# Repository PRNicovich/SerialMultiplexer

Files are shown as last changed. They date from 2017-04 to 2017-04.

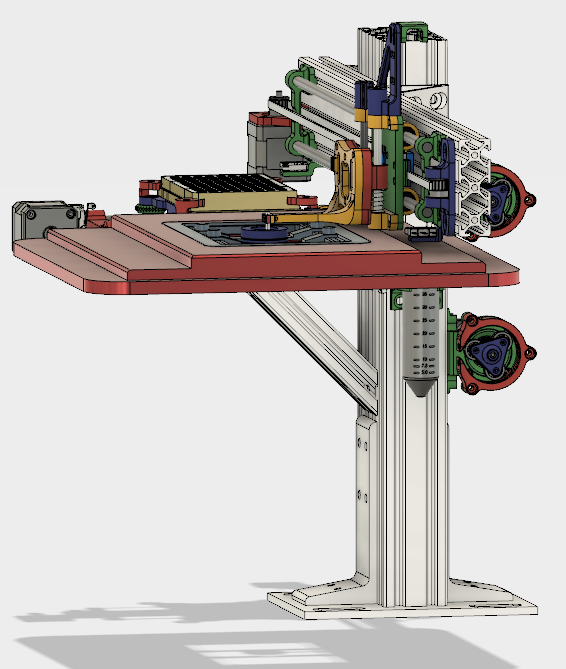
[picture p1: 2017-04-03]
Pics/Renderings/Full assembly right front.png

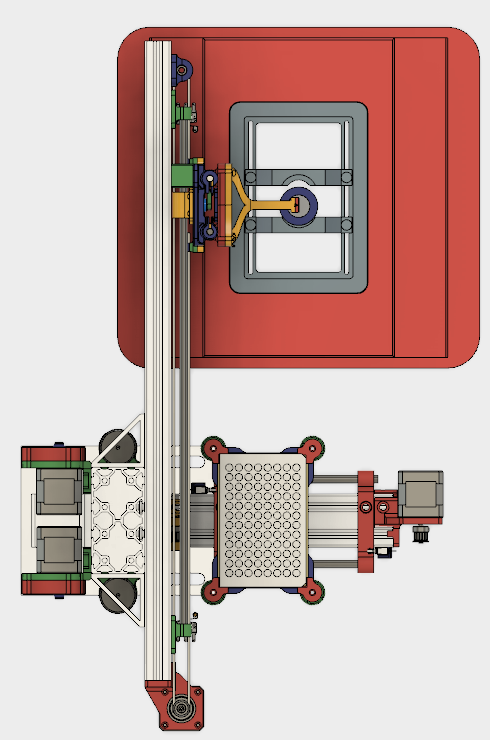
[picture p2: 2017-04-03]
Pics/Renderings/Full assembly top.png

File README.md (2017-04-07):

# Open source robot for liquid handing and serial multiplexing fluorescence microscopy

### Motivation

For fluorescence microscopy, a large limitation on the amount of data that can be extracted from a single sample is the number of targets that can be labeled within a sample.  Fluorophore spectral overlap limits this to around four targets in a typical setup, possibly up to ten if careful spectral demixing is done. In contrast, a single signalling pathway may contain a few hundred components.  Quantifying all of these components in a single sample would require an approach that increases the number of targets by an order of magnitude or more.  

One solution is to label targets in a sequential manner with probe signal nullification steps in between.  Target probes are introduced in sequential rounds, if possible without moving the sample off of the microscope.  After imaging, the probe signal can be removed either by stripping the probes, washing out the probe solution, or chemically or photo-bleaching the label fluorophore.  With this procedure the number of targets that can be probed is expanded with the number of rounds.  With a 4 color set-up and 10 rounds, for example, there are up to 40 target channels that can be captured in such an experiment.  With clever 'barcoding' schemes, this can even scale exponentially, rather than linearly, with the number of rounds.  

To accomplish this feat, a single sample must be processed through the labelling and stripping steps repeatedly. Doing so automatically avoids many hours of exceptionally tedious work and ultimately a more precise product.  For this a form of multi-channel liquid handling is required.  To further avoid spending tens of thousands of dollars on a project that was initially unsanctioned and unfunded, a low-cost solution is certainly a benefit.

## Approach 

The *in situ* automated liquid handing needs to be able to move a selected aliquot of solution from one place off of the microscope into the sample holder.  Then this aliquot needs to be removed, the sample washed with buffer, possibly multiple times, while removing the waste solution.  Then the cycle needs to repeat.  Were this done manually, solutions would be pre-mixed in microcentrifuge tubes or a well plate.  An operator would then remove solution from each well in turn and adding to the sample holder, interspersing washing and waste removal steps.  This would likely be done with a micropippetor and disposable tips.  

Recapitulating this closely with a robotics platform is certainly a straightforward approach.  The micropippetor could even be mounted on a gantry arm and moved between the reagent and sample locations.  Such an action is the basis of many pipetting robots.  However, the volume setting and tip ejection are motions adding extra complexity that may not be required.  If instead liquid was dosed out of a programmable pump through a reusable tip, the setting and ejection steps would be unnecessary.  The remaining motions are then to position this tip into the reagent well and then into the sample chamber with dosing via the pumps.  This forms the basis of the design here.

The liquid-handling head (actually made of 3 separate tips, detailed below) is on a carrier head.  This head has a servo motor for raising and lowering, essentially toggling between two positions.  The carrier is on a long axis that moves it from the reagent well plate location to the sample on the microscope, some distance (~450 mm) away.  The well plate is on a holder that places the base of this plate and the bottom of the sample holder in the same plane.  The well plate holder is on its own carrier on a shorter axis that allows a given row of the well plate to be selected (the first axis selects the column).  An aliquot is drawn into the liquid handling head by a pump, which then pushes to dispense this liquid at the sample.  A second tip in this head can dispense buffer from a reservoir, and a third withdraws waste.  The first pump operates in a toggle-like mode, with the second and third in a unidirectional motion only.  The grand total is then a servo, three "positioning" motors, and two "dispensing" motors. 

Turns out this list also makes a 3D printer.  The carrier axes correspond to XY, the reagent toggle pump the Z axis, and the buffer and waste pumps taking the role of a dual extruder.  The positioning precision of a hobby-level 3D printer is plenty for this application.  An open-source RAMPS controller built upon an Arduino Mega supports these 5 stepper motors, the servo, plus a bit of additional functionality, with communication over a USB serial with G code commands.  The design can capitalize on the 3D printer hobbyst community and the cheap components available for those projects.  These include the controller, motors, bearings, guide rods, and timing belts.  A bit of extruded T slot aluminum makes up the bulk of the skeleton, with the remaining parts being 3D printed on a desktop machine.

The bulk of the complex parts can be printed on a standard filament 3D printer.  This borrows quite bit again from the hobbyst 3D printer community, specifically the Reprap and Prusa projects.  Many of the components were highly inspired by analogous components in these projects.  

Controller code is based on Marlin (with configurating settings to work with this build) just as many Reprap printers.  The PC communicates with the controller through G code commands in this software.  A MATLAB class and demo scripts simplifying these operations will be included though one could imagine a custom fork of something like Repetier to drive the instrument.  From our perspective mounting the device within MicroManager or similar instrument-driving software is the eventual goal for integration into a microscope platform. 

To complete the liquid handling side of the machine, 3D printable peristaltic pumps were designed.  The use of the same stepper motors make these easy to control.  The controller is already set up to treat these as either the Z printer axis or a dual-head extruder.  The design uses skate bearings against flexible tubing to push along fluid.  These have no issue moving an appropriate amount of fluid in a reasonable time under PC control. There is a decent amount of pulsing but it is sufficient for moving fluid from one place to another. One could substitute these for syringe pumps or another, more precise, fluid-moving system if desired.  The Arduino has multiple serial ports exposed that could be addressed (or this could be handled on the PC side) to send commands to such pumps if not driving the motor directly. 

## Design considerations

The use of 3D printed parts and components is not the most precise way to do things.  The combination of rough parts and slop in cheap bearings is plenty to have extra motion above the theoretical resolution.  To address this, one must focus first on what precision is actually needed.  Here the XY positioning needs to be good enough to not hit the wall of the plate well.  The chosen steppers, drivers, and belt can theoretically hit 180 micrometer positioning.  Our tests show repeatability within 2-3x this, though periodic axis re-zeroing is a good idea to avoid missing step errors.  Still that is certainly precise enough to hit the middle of a well that's approximately 5 mm in diameter.

More precision is needed for the up-down motion of the needle carrier head.  Or, more correctly, the lower limit of this travel must be precise and repeatable to reach as close of the bottom of the well as possible to avoid wasting liquid (at the other end, as long as the needle is high enough up it doesn't matter where it is past that).  The same criterium means that solution removal and washes at the sample chamber can be more efficient.  There is an additional wrinkle in that the bottom of the sample chamber is a very thin, fragile glass coverslip.  Slamming into that repeatedly will lead to a crack and ruined experiment.  So we need a way to repeatably hit the same position without overshooting at the end of the downstroke for the bottom of the well and the bottom of the sample chamber. 

The second consideration for a "sloppy" system can be applied to simplify this issue, namely to leave enough adjustment to fine-tune or calibrate any residual imprecision out of the system.  The design is intended to hold the bottom of the well plate in the same plane as the bottom of the sample chamber.  This removes the need for separate positioning for the two locations, meaning there is only one bottom position for the needle carrier to hit.  The transverse X axis can be moved up and down on the vertical support member to roughly position the needle carrier in the proper vertical position for the associated microscope stage.  The well plate axis can slide along the same vertical member to bring the well plate in the same plane as the sample.  Finally there is a finer adjustment in the carrier head, where the linkage between the servo linkage arm can vertically translate in the needle carrier to bring the stop position in the proper alignment. 

Initially the linkage between the servo motor and the needle axis was a cam-follower mechanism.  The servo would rotate and push against a pair of springs around the bearing rods to lower the needle carrier.  This has the distinct advantage in that an imprecise rotator (a cheap servo) can lower to the same position very repeatedly.  If the cam is a constant diameter through a range at the end of the travel, as long as the rotation is somewhere in that range then the translation imprecision is removed.  Unfortunately finding appropriate springs of the proper diameter and length and compression force is difficult and time-consuming, so this approach was abandoned. 

The alternate approach was a more traditional linkage between the servo and needle carrier.  Now the servo rotational position is directly tied to the translation position.  The error in this rotatation is also directly linked.  In practice the cheap servo used does work within the repeatedly required. When moving long distances there is a considerable amount of rotational overshoot, however, which seems to be proportional to the distance traveled.  This may be minimized with a higher-quality motor or proper servo controller, but one work-around is to move in steps. The bulk of the motion can be done in a first step, but stopping early so that overrotation of the servo does not result in overshooting the final target.  A second smaller step brings the needle carrier to the final position with much lower overshoot.  This effect is visible in the included video of the instrument in action where the vertical motion of the needle carrier is clearly done in two motions.

Motor positions and travel speeds can be set in software.  These need to be calibrated for the given build.  For travel of the axes this is straighforward and in millimeters.  Rotational position of the servo and translation of dispensor distance to volume units will need to be done empirically, but this is relatively straightforward to establish. 

## Repo contents

.\STEP Files\ - STEP files of full assembly and of the custom base plate to mount to a metric optical table.  

.\STL Files\ - All files for 3D printing.  These are ready to go into your favorite slicer software to generate 3D printer machine code.

.\Pics\ - Photos and renderings of the completed assembly.  A video of the robot motion testing in action is included. 

.\Hardware\ - Bill of Materials for all items to be purchased for this build.  This includes all fasteners and other hardware omitted in the STEP files.  A measured drawing for the base plate is included, ready to be sent to your local machine shop (or give making it yourself a shot). 

.\Code\ - Configuration files for Marlin driver for Arduino and MATLAB PC-side MATLAB code included.  The PC does a small amount of processing and primarily relays Gcode over a serial connection to the Arduino.  Should be straightforward to port to Python, Micromanager Beanshell Java, or whatever other language you may prefer.

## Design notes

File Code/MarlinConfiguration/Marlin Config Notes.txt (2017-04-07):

Download latest stable release of Marlin from associated Github repo:

https://github.com/MarlinFirmware/Marlin/releases

Configuration guide can be found here:

https://github.com/MarlinFirmware/Marlin/wiki/Marlin-Configuration

The two files in this folder, Configuration.h and Configuration_adv.h, are those from the original implementation of this build.  You can replace the default Marlin config files with these as a good starting point.  These include important details about temperature sensors (or the lack thereof) and end stops. Further tweaks can be made if desired to tune specifically for your project.

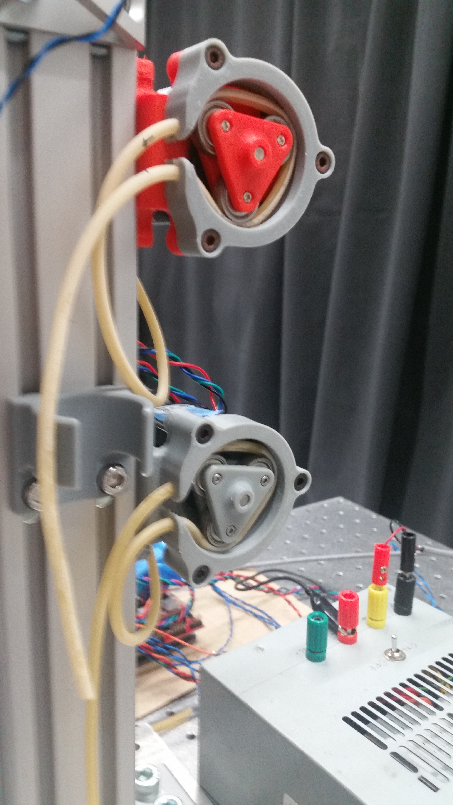
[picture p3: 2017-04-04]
Pics/Photos/PumpHeads.jpg

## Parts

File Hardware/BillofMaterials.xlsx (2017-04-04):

Category | Description | Supplier | Supplier part no | Qty | Price per | Total cost | Notes
T slot profiles | 25 mm x 75 mm T slot | 80/20 | 25-2576 | 1 | $19.98 | $19.98 | 600 mm; tap all holes on ONE end
 | 50 mm x 100 mm T slot | 80/20 | 25-5010 | 1 | $19.50 | $19.50 | 435 mm
 | Angle anchor bracket | 80/20 | 25-2416 | 2 | $11.05 | $22.10
 | 4 bolt angle support | 80/20 | 25-4138 | 2 | $7.45 | $14.90
 | 45 degree angle profile | 80/20 | 25-2566 | 1 | $14.95 | $14.95
 | 25 mm x 50 mm T slot | 80/20 | 25-2550 | 1 | $12.91 | $12.91 | 233 mm; tap holes on one end; contersink 2 holes on wide face other end
 | Cam connectors | 80/20 | 25-3363 | 2 | $4.00 | $8.00
 | T slot nuts | 80/20 | 25-1962 | 30 | $0.23 | $6.90
 | T slot nuts, double | 80/20 | 25-1941 | 12 | $0.53 | $6.36
Motion surfaces | LM8UU bearings | CNC Superstore | LM8UU | 4 | $1.49 | $5.96
 | LM6UU bearings | CNC Superstore | LM6UU | 2 | $1.49 | $2.98
 | SKF 625 bearings | VXB | 625-Z | 13 | $1.49 | $19.37 | Open or sealed OK
 | 682 bearings | VXB | KIT7420 | 2 | $6.49 | $12.98 | Open > sealed
 | GT2 pulleys | MakerTechStore | n/a | 4 | $3.00 | $12.00 | 16 teeth; 5 mm bore
 | GT2 belt | MakerTechStore | n/a | 7 | $2.50 | $17.50 | 7 ft, 2 m; 2 mm pitch
 | Bearing rods; 6 mm x 100 mm | VXB | SNS6X100MM-NB | 2 | $19.95 | $39.90 | 100-150 mm
 | Bearing rods; 8 mm x 500 mm | VXB | KIT11866 | 2 | $19.95 | $39.90 | 480-550 mm (product is 495 mm)
 | Bearing rods; 8 mm x 150 mm | eBay | various | 2 | $5.00 | $10.00 | 150-170 mm
 | Well axis clamp springs | McMaster-Carr | 9657K81 | 4 | $5.43 | $21.72 | 3.5-4.5 mm dia; 3-6 mm compressed length
Motors | NEMA 17 steppers | Various | Various | 5 | $20.00 | $100.00 | 1.8 deg step (200/rev); 45 N-cm (64 oz-in)
 | Micro servo | Various | Various | 1 | $6.00 | $6.00 | 5V; 9g; Tower Pro SG92R or similar
Fasteners | M10 SHCS | McMaster-Carr | 91290A127 | 4 | $7.29 | $7.29 | 14 mm, pk of 25
 | M6 SHCS | McMaster-Carr | 91290A330 | 8 | $7.28 | $7.28 | 25 mm, pk of 50
 | M6 BHCS | McMaster-Carr | 91239A316 | 60 | $10.14 | $10.14 | 10 mm, pk of 100
 | M5 SHCS | McMaster-Carr | 91292A193 | 2 | $5.37 | $5.37 | 35 mm, pk of 25
 | M4 SHCS | McMaster-Carr | 91292A118 | 10 | $7.20 | $7.20 | 16 mm, pk of 100
 | M3 SHCS | McMaster-Carr | 91292A113 | 50 | $4.40 | $4.40 | 10 mm, pk of 100
 | M3 SHCS | McMaster-Carr | 91292A020 | 12 | $6.40 | $6.40 | 25 mm, pk of 100
 | M2 SHCS | McMaster-Carr | 91292A834 | 8 | $3.64 | $3.64 | 12 mm, pk of 100
 | M2 SHCS | McMaster-Carr | 91292A832 | 18 | $6.00 | $6.00 | 8 mm, pk of 100
 | M2 SHCS | McMaster-Carr | 92290A012 | 2 | $6.72 | $6.72 | 5 mm, pk of 100
 | M2 washers | McMaster-Carr | 93475A195 | 2 | $1.06 | $1.06 | pk of 100
 | M2 nuts | McMaster-Carr | 90592A004 | 21 | $1.04 | $1.04 | pk of 100
 | M3 washers | McMaster-Carr | 93475A210 | 4 | $1.62 | $1.62 | pk of 100
 | M3 nuts | McMaster-Carr | 90591A250 | 50 | $2.06 | $2.06 | pk of 100
 | M4 nuts | McMaster-Carr | 90591A255 | 10 | $2.28 | $2.28 | pk of 100
 | M5 nuts | McMaster-Carr | 90591A260 | 2 | $2.61 | $2.61 | pk of 100
Cable carrier | 10 x 15 mm segmented carrier | Sparkfun | 13207 | 1 | $10.95 | $10.95
Tubing | 2 mm x 4 mm tubing | McMaster-Carr | 5186T11 | 20 | $0.65 | $13.00 | 3 m (20 ft); 2 mm ID, 4 mm OD
 | 1.0 mm x 2 mm tubing | McMaster-Carr | 51825K41 | 25 | $0.21 | $5.25 | 25 ft; 1 mm ID, 2 mm OD
 | 18ga stainless tubing | McMaster-Carr | 50415K38 | 1 | $8.80 |  | 0.5 m; 18 gauge blunt needles w/ flange cut work well!
Controller | RAMPS 1.4 board | Various | -- | 1 | $10.00 | $10.00
 | Arduino Mega | Various | ATmega2560 R3 board | 1 | $9.00 | $9.00
 | Stepper controller | Various | A4988 module | 5 | $1.50 | $7.50
 | 5v/12v power supply | Various | -- | 1 | -- | -- | home-built from PC PSU
 | Connection wires | Various | -- | varies | $10.00 | $10.00 | est
 | Spade connector (F) | Mouser | 534-1252 | 8 | $0.15 | $1.20 | Many similar connectors
Limit switches | Omron D2SW‑P2L2T | Mouser | 653-D2SW-P2L2T | 4 | $3.04 | $12.16
Mounting plate | Machined mounting plate | ProtoLabs | -- | 1 | $251.39 | $251.39 | See ..\STEP Files\ModifiedBase.stp, .\OpticalTableTslotMountingPlate_Sheet1.pdf
 |  |  |  |  | Total | $819.47 | ← Surely an over-estimate, as: - the mounting plate can be made to MUCH larger tolerance than quoted - steppers cheaper if bought in a larger group - likely can find cheaper source for bearing shafts - most screws ordered in excessively large packs

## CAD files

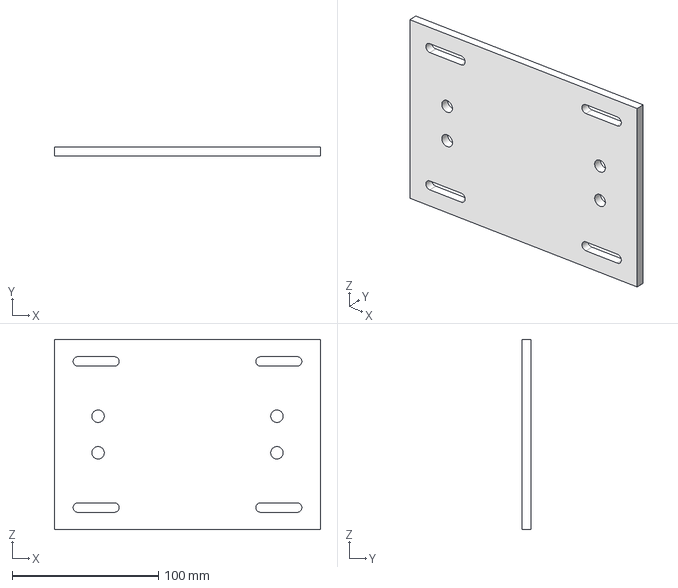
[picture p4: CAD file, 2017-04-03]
STEP Files/ModifiedBase.stp
182.0 x 6.00 x 130.0 mm

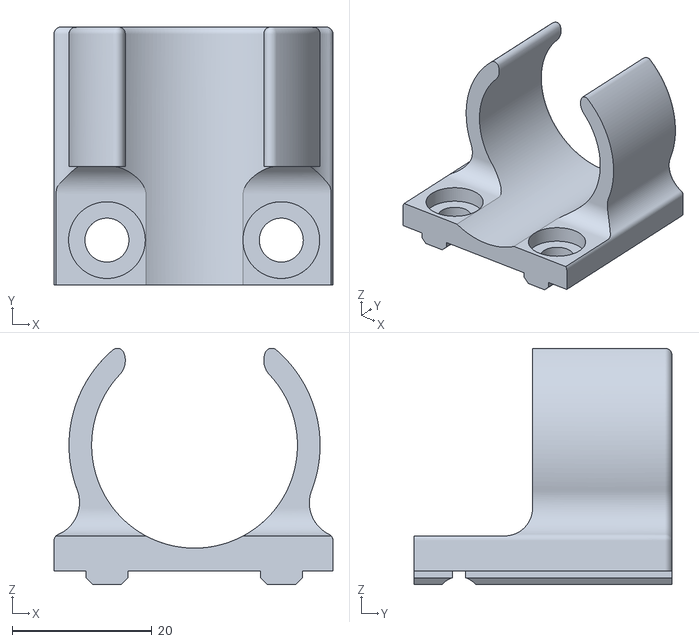
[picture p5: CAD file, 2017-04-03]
STL Files/Attachments/50mLTubeHolder.stl
40.0 x 37.0 x 33.9

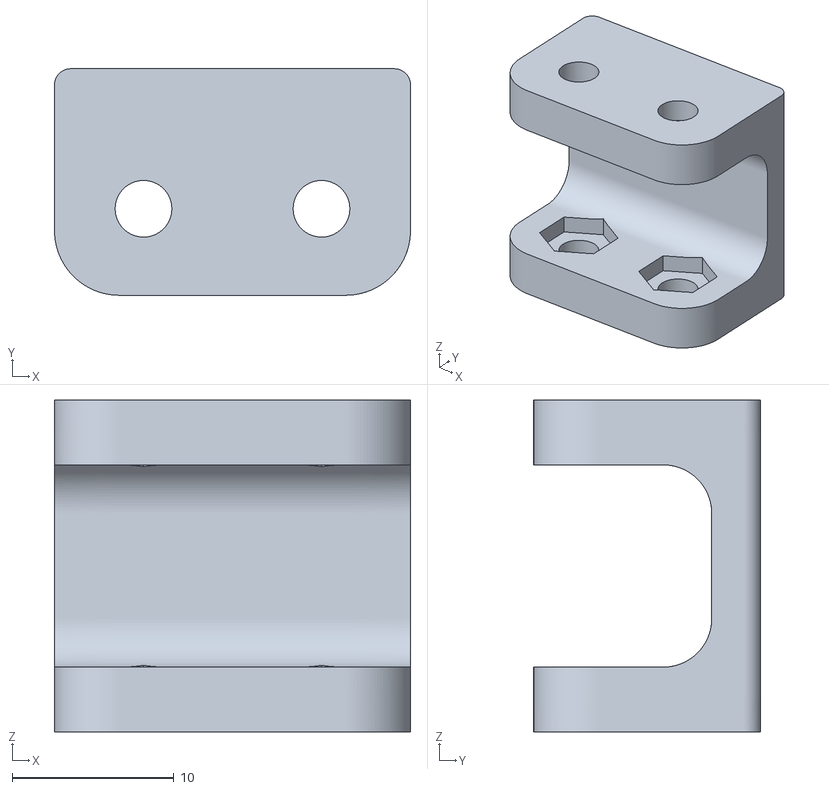
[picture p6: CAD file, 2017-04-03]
STL Files/CarrierAxis/Cable carrier to cable snake.stl
22.0 x 14.0 x 20.5

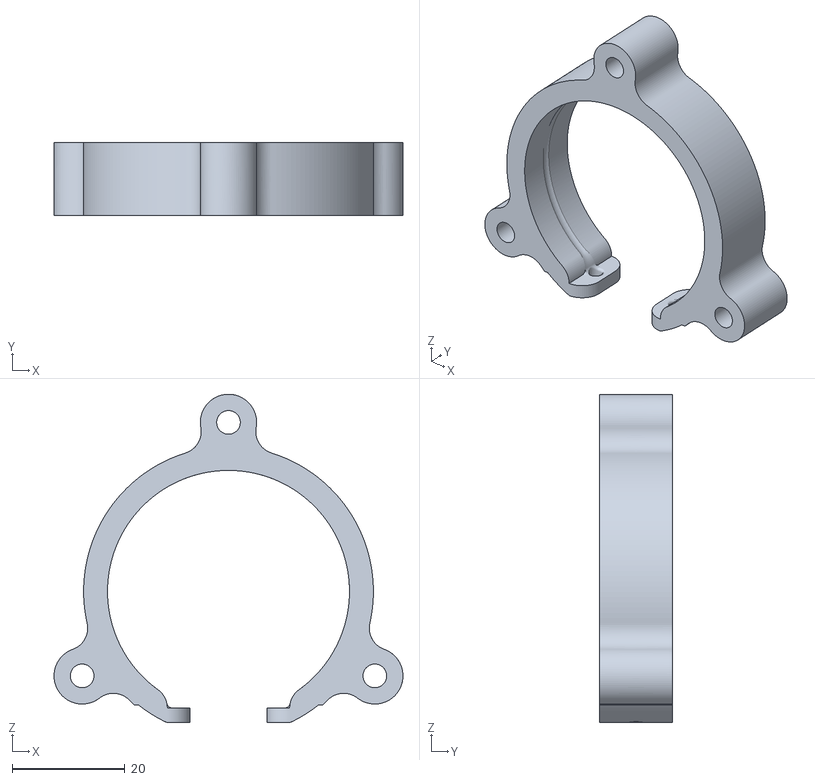
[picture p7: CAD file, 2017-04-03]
STL Files/PerfusionPump/PumpChassis.stl
62.0 x 13.0 x 58.3

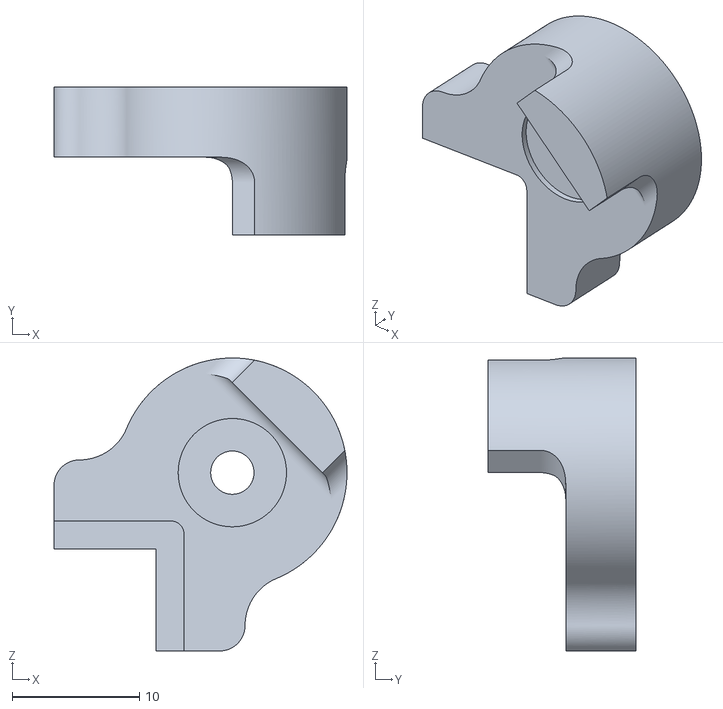
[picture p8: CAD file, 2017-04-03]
STL Files/WellPlateAxis/WellPlateClampRetry.stl
23.0 x 11.6 x 23.0

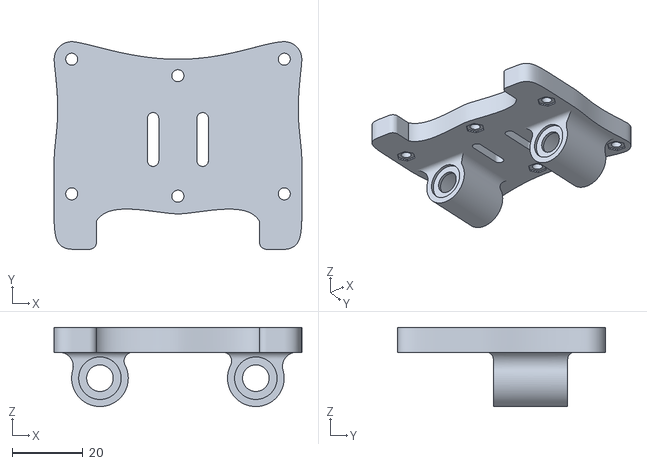
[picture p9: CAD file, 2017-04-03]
STL Files/CarrierAxis/NeedleCarrier.stl
70.0 x 58.6 x 22.3

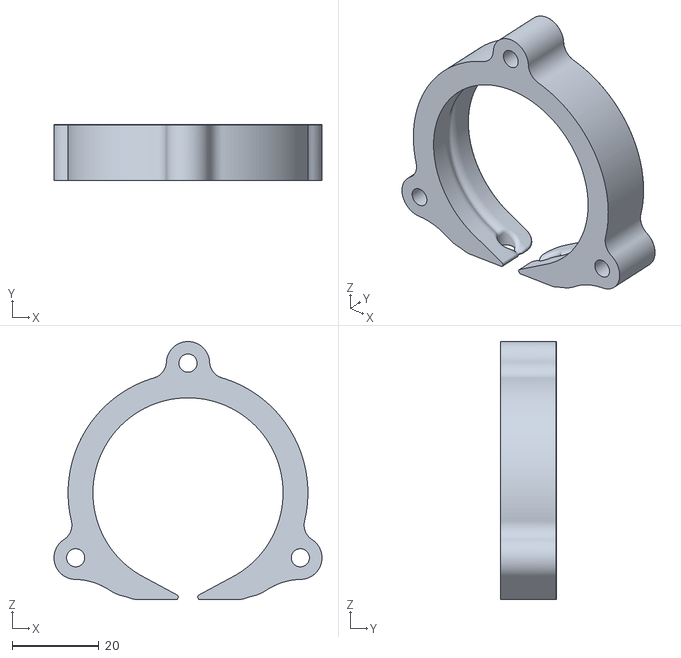
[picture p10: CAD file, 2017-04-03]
STL Files/PerfusionPump/PumpChassis4mmTubing.stl
62.0 x 13.0 x 59.6

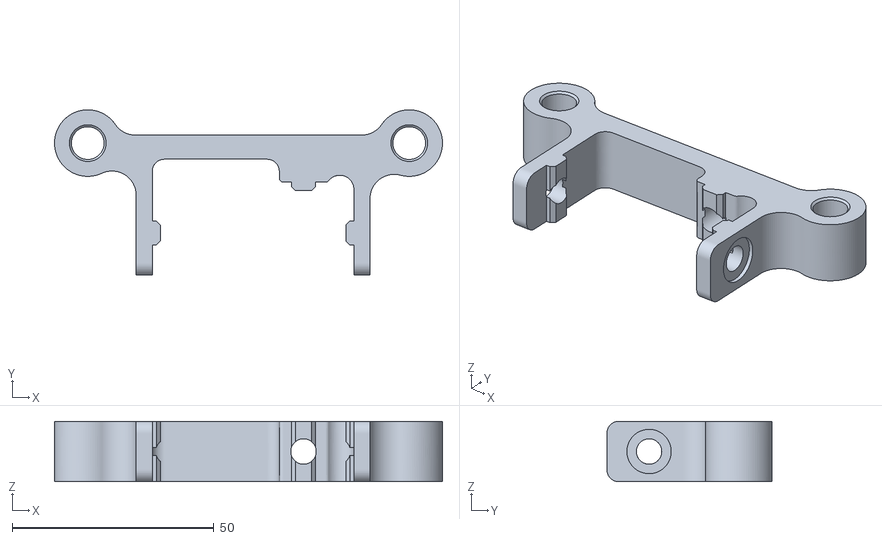
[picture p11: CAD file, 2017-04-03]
STL Files/WellPlateAxis/WellPlate8mmRodMount.stl
96.2 x 41.0 x 15.0

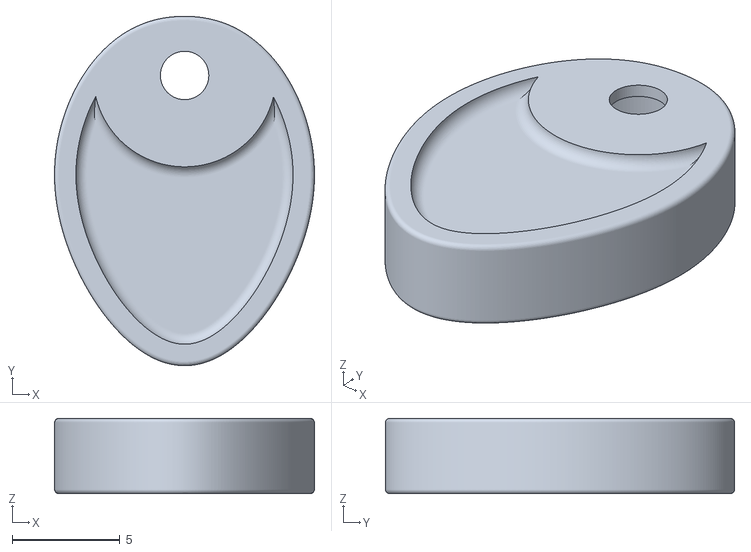
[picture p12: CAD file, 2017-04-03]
STL Files/CarrierAxis/servoCam5mm.stl
12.1 x 16.2 x 3.50

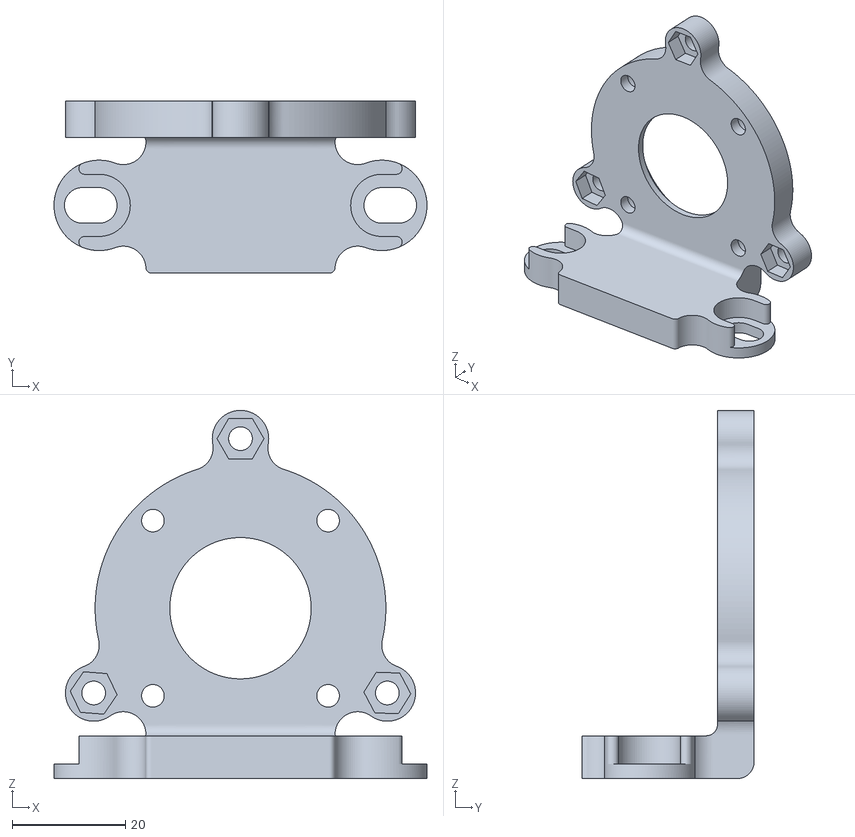
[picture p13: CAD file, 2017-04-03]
STL Files/PerfusionPump/PumpMotorMount.stl
66.0 x 30.5 x 65.1

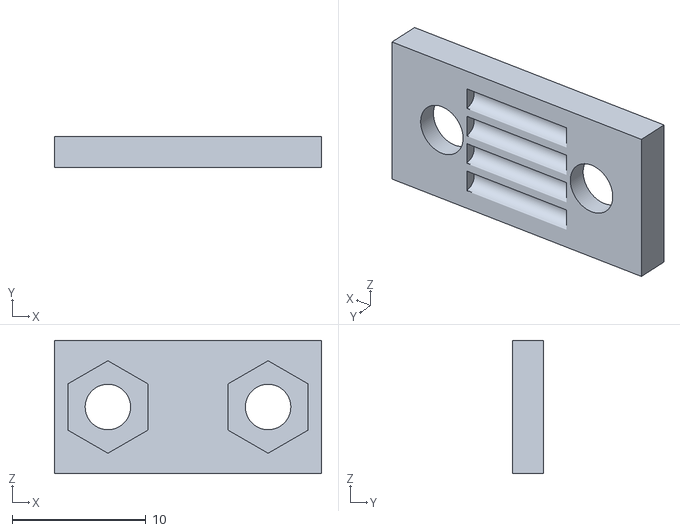
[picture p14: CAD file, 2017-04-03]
STL Files/WellPlateAxis/WellPlateBeltClamp.stl
20.0 x 2.32 x 10.0

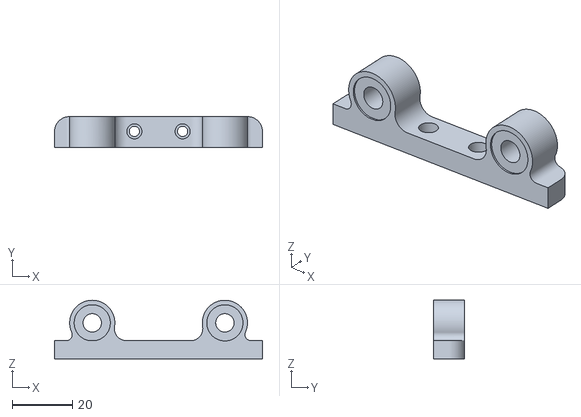
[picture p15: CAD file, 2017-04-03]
STL Files/CarrierAxis/Carrier6mmRodClampUpper.stl
69.0 x 10.2 x 19.4

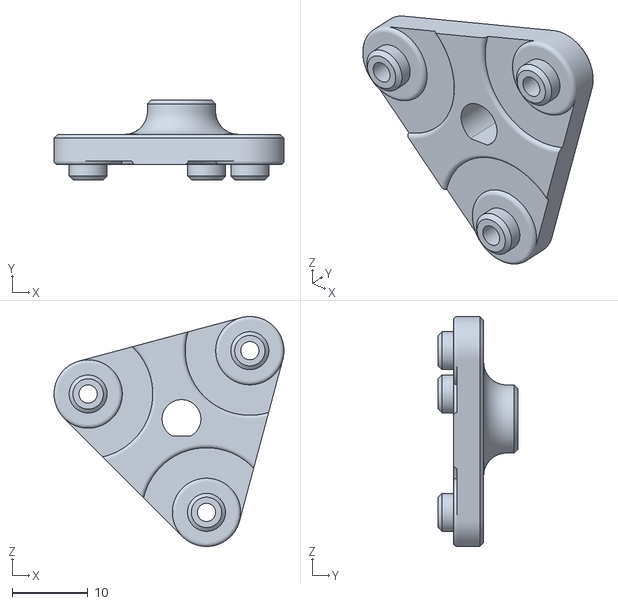
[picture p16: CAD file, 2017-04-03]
STL Files/PerfusionPump/UpperBearingCarrier.stl
30.3 x 10.5 x 30.3

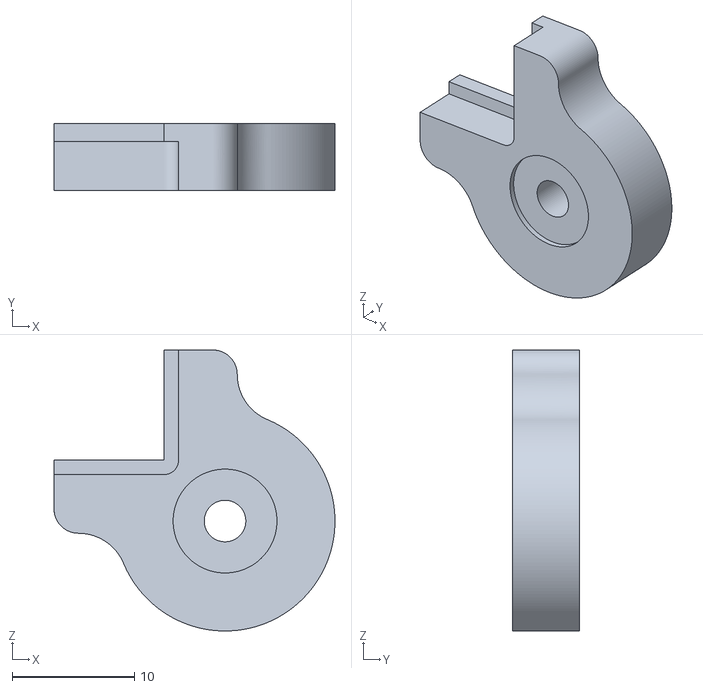
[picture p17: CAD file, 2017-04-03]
STL Files/WellPlateAxis/WellPlateClamp.stl
23.0 x 5.50 x 23.0

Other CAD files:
STL Files/CarrierAxis/servoCam46.stl
STL Files/PerfusionPump/LowerBearingCarrier.stl
STL Files/WellPlateAxis/WellPlateIdlerPulleyMount.stl
STL Files/CarrierAxis/CarrierBeltClampLeft.stl
STL Files/CarrierAxis/Cable carrier.stl
STL Files/CarrierAxis/Carraige v2.stl
STL Files/CarrierAxis/Carraige.stl
STL Files/CarrierAxis/CarriageBearingHolder.stl
STL Files/CarrierAxis/Carrier6mmRodClampLower v2.stl
STL Files/CarrierAxis/Carrier6mmRodClampLower.stl
STL Files/CarrierAxis/Carrier6mmRodClampUpper v2.stl
STL Files/CarrierAxis/CarrierAxis8mmRodClamp.stl
STL Files/CarrierAxis/CarrierBeltClampRight.stl
STL Files/CarrierAxis/EndSwitchMount.stl
STL Files/CarrierAxis/IdlerPulleyMount.stl
STL Files/CarrierAxis/MotorMount.stl
STL Files/CarrierAxis/NeedleCarrier v2.stl
STL Files/CarrierAxis/NeedleClamp.stl
STL Files/CarrierAxis/NeedleNose v2.stl
STL Files/CarrierAxis/NeedleNose.stl
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

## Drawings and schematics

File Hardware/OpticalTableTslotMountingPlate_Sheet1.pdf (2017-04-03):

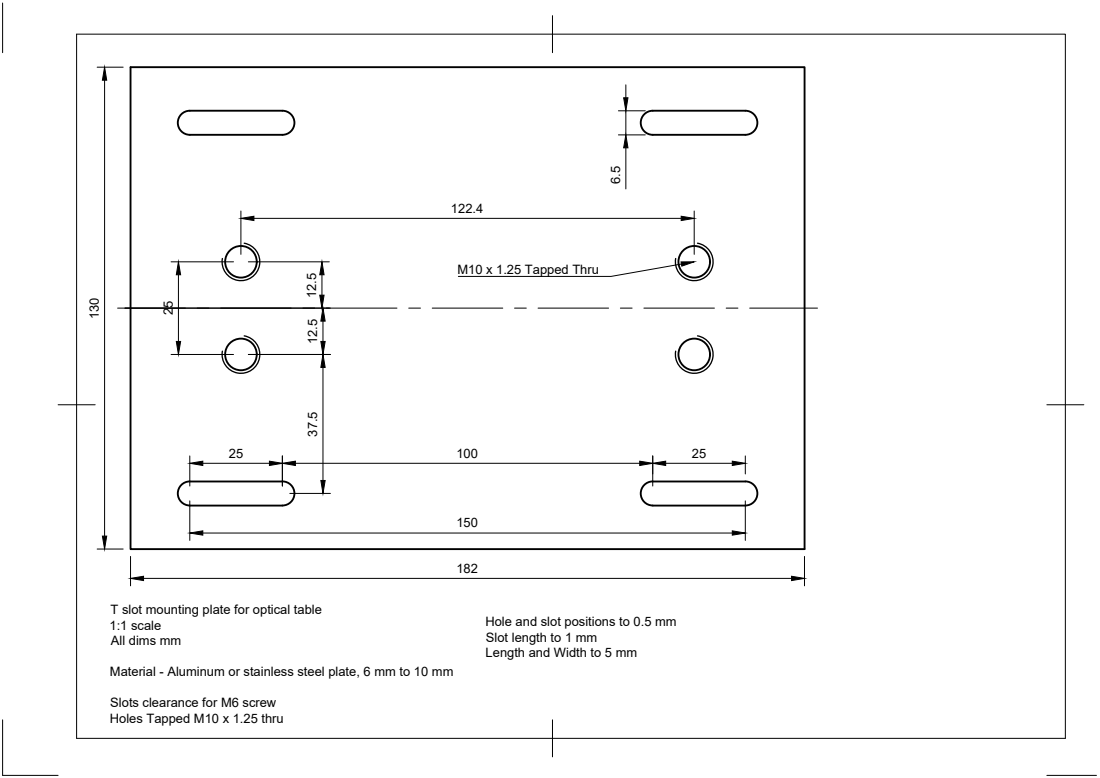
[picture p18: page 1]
M10 x 1.25 Tapped Thru 6.5

T slot mounting plate for optical table
1:1 scale
All dims mm

Hole and slot positions to 0.5 mm
Slot length to 1 mm
Length and Width to 5 mm

Material - Aluminum or stainless steel plate, 6 mm to 10 mm

Slots clearance for M6 screw
Holes Tapped M10 x 1.25 thru

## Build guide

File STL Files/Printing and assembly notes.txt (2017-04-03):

# Printing

All STL files were printed on a Zortrax M200 filament printer with Ultra-T filament.  Printing with the minimum layer thickness and a heavy infill is appropriate for those parts that will see force or strain.  Many parts can be printed with larger layer thicknesses and lower infill for speed and efficient use of fillament. 

Care is needed in orienting parts on the print bed.  Those parts interfacing with bearing or rod surfaces are largely press-fit and require a close tolerance for those dimensions.  Having the axis of the cylinder that makes up this interaction be perpendicular to the print bed is the best option whenever possible.

A number of these parts need some clean-up for support material but also for clearance of bearings or screw heads.  A sharp knife is sufficient in most cases.  

# Assembly
All fasteners are metric cap screws.  The majority of these are M3 hex head cap screws, with a few M2, M4, and a couple M5 included. A variety of lengths are required. M6 button head hex cap screws are used to secure the T slot aluminum together and mount parts to those components. 

The press-fit assembly can be done on a vise or with a c-clamp. Hammering these fits home is possible but more likely to cause a broken part.

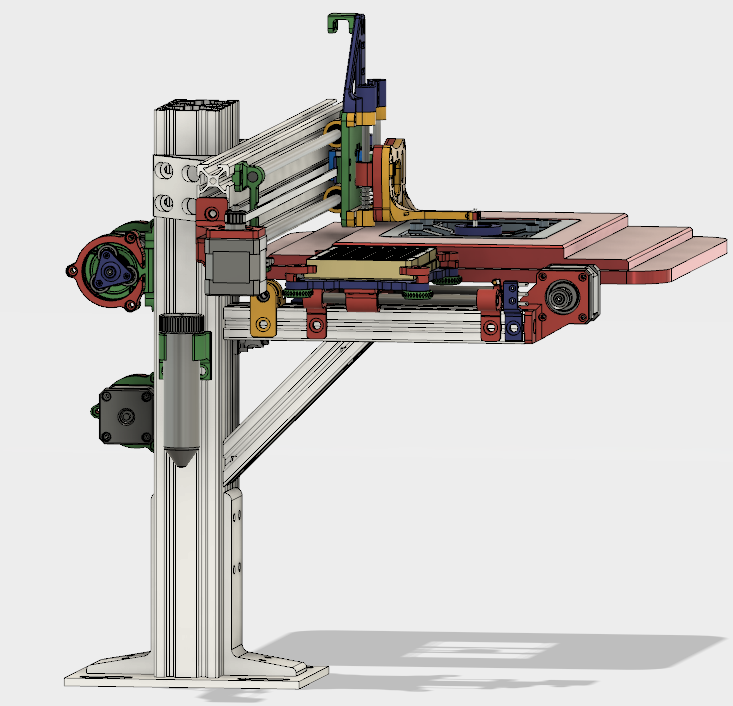
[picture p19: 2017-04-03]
Pics/Renderings/Full assembly front left.png

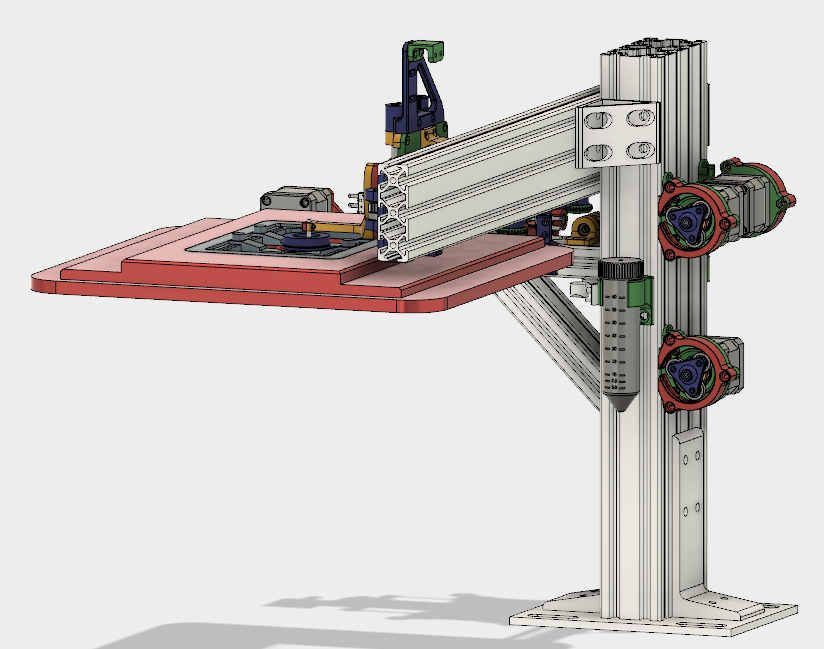
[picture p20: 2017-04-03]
Pics/Renderings/Full assembly right rear.png

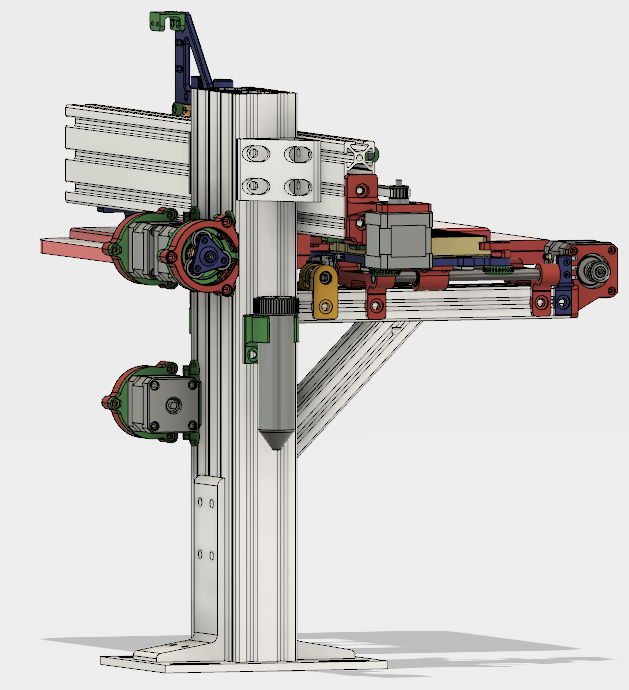
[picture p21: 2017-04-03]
Pics/Renderings/Full assembly rear left.png

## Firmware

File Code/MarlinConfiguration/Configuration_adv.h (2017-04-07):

/**
 * Marlin 3D Printer Firmware
 * Copyright (C) 2016 MarlinFirmware [https://github.com/MarlinFirmware/Marlin]
 *
 * Based on Sprinter and grbl.
 * Copyright (C) 2011 Camiel Gubbels / Erik van der Zalm
 *
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
 */

/**
 * Configuration_adv.h
 *
 * Advanced settings.
 * Only change these if you know exactly what you're doing.
 * Some of these settings can damage your printer if improperly set!
 *
 * Basic settings can be found in Configuration.h
 *
 */
#ifndef CONFIGURATION_ADV_H
#define CONFIGURATION_ADV_H

/**
 *
 *  ***********************************
 *  **  ATTENTION TO ALL DEVELOPERS  **
 *  ***********************************
 *
 * You must increment this version number for every significant change such as,
 * but not limited to: ADD, DELETE RENAME OR REPURPOSE any directive/option.
 *
 * Note: Update also Version.h !
 */
#define CONFIGURATION_ADV_H_VERSION 010100

// @section temperature

//===========================================================================
//=============================Thermal Settings  ============================
//===========================================================================

#if DISABLED(PIDTEMPBED)
  #define BED_CHECK_INTERVAL 5000 // ms between checks in bang-bang control
  #if ENABLED(BED_LIMIT_SWITCHING)
    #define BED_HYSTERESIS 2 // Only disable heating if T>target+BED_HYSTERESIS and enable heating if T>target-BED_HYSTERESIS
  #endif
#endif

/**
 * Thermal Protection protects your printer from damage and fire if a
 * thermistor falls out or temperature sensors fail in any way.
 *
 * The issue: If a thermistor falls out or a temperature sensor fails,
 * Marlin can no longer sense the actual temperature. Since a disconnected
 * thermistor reads as a low temperature, the firmware will keep the heater on.
 *
 * The solution: Once the temperature reaches the target, start observing.
 * If the temperature stays too far below the target (hysteresis) for too long (period),
 * the firmware will halt the machine as a safety precaution.
 *
 * If you get false positives for "Thermal Runaway" increase THERMAL_PROTECTION_HYSTERESIS and/or THERMAL_PROTECTION_PERIOD
 */
#if ENABLED(THERMAL_PROTECTION_HOTENDS)
  #define THERMAL_PROTECTION_PERIOD 40        // Seconds
  #define THERMAL_PROTECTION_HYSTERESIS 4     // Degrees Celsius

  /**
   * Whenever an M104 or M109 increases the target temperature the firmware will wait for the
   * WATCH_TEMP_PERIOD to expire, and if the temperature hasn't increased by WATCH_TEMP_INCREASE
   * degrees, the machine is halted, requiring a hard reset. This test restarts with any M104/M109,
   * but only if the current temperature is far enough below the target for a reliable test.
   *
   * If you get false positives for "Heating failed" increase WATCH_TEMP_PERIOD and/or decrease WATCH_TEMP_INCREASE
   * WATCH_TEMP_INCREASE should not be below 2.
   */
  #define WATCH_TEMP_PERIOD 20                // Seconds
  #define WATCH_TEMP_INCREASE 2               // Degrees Celsius
#endif

/**
 * Thermal Protection parameters for the bed are just as above for hotends.
 */
#if ENABLED(THERMAL_PROTECTION_BED)
  #define THERMAL_PROTECTION_BED_PERIOD 20    // Seconds
  #define THERMAL_PROTECTION_BED_HYSTERESIS 2 // Degrees Celsius

  /**
   * Whenever an M140 or M190 increases the target temperature the firmware will wait for the
   * WATCH_BED_TEMP_PERIOD to expire, and if the temperature hasn't increased by WATCH_BED_TEMP_INCREASE
   * degrees, the machine is halted, requiring a hard reset. This test restarts with any M140/M190,
   * but only if the current temperature is far enough below the target for a reliable test.
   *
   * If you get too many "Heating failed" errors, increase WATCH_BED_TEMP_PERIOD and/or decrease
   * WATCH_BED_TEMP_INCREASE. (WATCH_BED_TEMP_INCREASE should not be below 2.)
   */
  #define WATCH_BED_TEMP_PERIOD 60                // Seconds
  #define WATCH_BED_TEMP_INCREASE 2               // Degrees Celsius
#endif

#if ENABLED(PIDTEMP)
  // this adds an experimental additional term to the heating power, proportional to the extrusion speed.
  // if Kc is chosen well, the additional required power due to increased melting should be compensated.
  //#define PID_EXTRUSION_SCALING
  #if ENABLED(PID_EXTRUSION_SCALING)
    #define DEFAULT_Kc (100) //heating power=Kc*(e_speed)
    #define LPQ_MAX_LEN 50
  #endif
#endif

/**
 * Automatic Temperature:
 * The hotend target temperature is calculated by all the buffered lines of gcode.
 * The maximum buffered steps/sec of the extruder motor is called "se".
 * Start autotemp mode with M109 S<mintemp> B<maxtemp> F<factor>
 * The target temperature is set to mintemp+factor*se[steps/sec] and is limited by
 * mintemp and maxtemp. Turn this off by executing M109 without F*
 * Also, if the temperature is set to a value below mintemp, it will not be changed by autotemp.
 * On an Ultimaker, some initial testing worked with M109 S215 B260 F1 in the start.gcode
 */
#define AUTOTEMP
#if ENABLED(AUTOTEMP)
  #define AUTOTEMP_OLDWEIGHT 0.98
#endif

//Show Temperature ADC value
//The M105 command return, besides traditional information, the ADC value read from temperature sensors.
//#define SHOW_TEMP_ADC_VALUES

/**
 * High Temperature Thermistor Support
 *
 * Thermistors able to support high temperature tend to have a hard time getting
 * good readings at room and lower temperatures. This means HEATER_X_RAW_LO_TEMP
 * will probably be caught when the heating element first turns on during the
 * preheating process, which will trigger a min_temp_error as a safety measure
 * and force stop everything.
 * To circumvent this limitation, we allow for a preheat time (during which,
 * min_temp_error won't be triggered) and add a min_temp buffer to handle
 * aberrant readings.
 *
 * If you want to enable this feature for your hotend thermistor(s)
 * uncomment and set values > 0 in the constants below
 */

// The number of consecutive low temperature errors that can occur
// before a min_temp_error is triggered. (Shouldn't be more than 10.)
//#define MAX_CONSECUTIVE_LOW_TEMPERATURE_ERROR_ALLOWED 0

// The number of milliseconds a hotend will preheat before starting to check
// the temperature. This value should NOT be set to the time it takes the
// hot end to reach the target temperature, but the time it takes to reach
// the minimum temperature your thermistor can read. The lower the better/safer.
// This shouldn't need to be more than 30 seconds (30000)
//#define MILLISECONDS_PREHEAT_TIME 0

// @section extruder

//  extruder run-out prevention.
//if the machine is idle, and the temperature over MINTEMP, every couple of SECONDS some filament is extruded
//#define EXTRUDER_RUNOUT_PREVENT
#define EXTRUDER_RUNOUT_MINTEMP 190
#define EXTRUDER_RUNOUT_SECONDS 30
#define EXTRUDER_RUNOUT_ESTEPS 14   // mm filament
#define EXTRUDER_RUNOUT_SPEED 1500  // extrusion speed
#define EXTRUDER_RUNOUT_EXTRUDE 100

// @section temperature

//These defines help to calibrate the AD595 sensor in case you get wrong temperature measurements.
//The measured temperature is defined as "actualTemp = (measuredTemp * TEMP_SENSOR_AD595_GAIN) + TEMP_SENSOR_AD595_OFFSET"
#define TEMP_SENSOR_AD595_OFFSET 0.0
#define TEMP_SENSOR_AD595_GAIN   1.0

//This is for controlling a fan to cool down the stepper drivers
//it will turn on when any driver is enabled
//and turn off after the set amount of seconds from last driver being disabled again
#define CONTROLLERFAN_PIN -1 //Pin used for the fan to cool controller (-1 to disable)
#define CONTROLLERFAN_SECS 60 //How many seconds, after all motors were disabled, the fan should run
#define CONTROLLERFAN_SPEED 255  // == full speed

// When first starting the main fan, run it at full speed for the
// given number of milliseconds.  This gets the fan spinning reliably
// before setting a PWM value. (Does not work with software PWM for fan on Sanguinololu)
//#define FAN_KICKSTART_TIME 100

// This defines the minimal speed for the main fan, run in PWM mode
// to enable uncomment and set minimal PWM speed for reliable running (1-255)
// if fan speed is [1 - (FAN_MIN_PWM-1)] it is set to FAN_MIN_PWM
//#define FAN_MIN_PWM 50

// @section extruder

// Extruder cooling fans
// Configure fan pin outputs to automatically turn on/off when the associated
// extruder temperature is above/below EXTRUDER_AUTO_FAN_TEMPERATURE.
// Multiple extruders can be assigned to the same pin in which case
// the fan will turn on when any selected extruder is above the threshold.
#define EXTRUDER_0_AUTO_FAN_PIN -1
#define EXTRUDER_1_AUTO_FAN_PIN -1
#define EXTRUDER_2_AUTO_FAN_PIN -1
#define EXTRUDER_3_AUTO_FAN_PIN -1
#define EXTRUDER_AUTO_FAN_TEMPERATURE 50
#define EXTRUDER_AUTO_FAN_SPEED   255  // == full speed

//===========================================================================
//============================ Mechanical Settings ==========================
//===========================================================================

// @section homing

// If you want endstops to stay on (by default) even when not homing
// enable this option. Override at any time with M120, M121.
#define ENDSTOPS_ALWAYS_ON_DEFAULT

// @section extras

//#define Z_LATE_ENABLE // Enable Z the last moment. Needed if your Z driver overheats.

// Dual X Steppers
// Uncomment this option to drive two X axis motors.
// The next unused E driver will be assigned to the second X stepper.
//#define X_DUAL_STEPPER_DRIVERS
#if ENABLED(X_DUAL_STEPPER_DRIVERS)
  // Set true if the two X motors need to rotate in opposite directions
  #define INVERT_X2_VS_X_DIR true
#endif


// Dual Y Steppers
// Uncomment this option to drive two Y axis motors.
// The next unused E driver will be assigned to the second Y stepper.
//#define Y_DUAL_STEPPER_DRIVERS
#if ENABLED(Y_DUAL_STEPPER_DRIVERS)
  // Set true if the two Y motors need to rotate in opposite directions
  #define INVERT_Y2_VS_Y_DIR true
#endif

// A single Z stepper driver is usually used to drive 2 stepper motors.
// Uncomment this option to use a separate stepper driver for each Z axis motor.
// The next unused E driver will be assigned to the second Z stepper.
//#define Z_DUAL_STEPPER_DRIVERS

#if ENABLED(Z_DUAL_STEPPER_DRIVERS)

  // Z_DUAL_ENDSTOPS is a feature to enable the use of 2 endstops for both Z steppers - Let's call them Z stepper and Z2 stepper.
  // That way the machine is capable to align the bed during home, since both Z steppers are homed.
  // There is also an implementation of M666 (software endstops adjustment) to this feature.
  // After Z homing, this adjustment is applied to just one of the steppers in order to align the bed.
  // One just need to home the Z axis and measure the distance difference between both Z axis and apply the math: Z adjust = Z - Z2.
  // If the Z stepper axis is closer to the bed, the measure Z > Z2 (yes, it is.. think about it) and the Z adjust would be positive.
  // Play a little bit with small adjustments (0.5mm) and check the behaviour.
  // The M119 (endstops report) will start reporting the Z2 Endstop as well.

  //#define Z_DUAL_ENDSTOPS

  #if ENABLED(Z_DUAL_ENDSTOPS)
    #define Z2_USE_ENDSTOP _XMAX_
  #endif

#endif // Z_DUAL_STEPPER_DRIVERS
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

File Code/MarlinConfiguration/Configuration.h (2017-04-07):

/**
 * Marlin 3D Printer Firmware
 * Copyright (C) 2016 MarlinFirmware [https://github.com/MarlinFirmware/Marlin]
 *
 * Based on Sprinter and grbl.
 * Copyright (C) 2011 Camiel Gubbels / Erik van der Zalm
 *
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
 */

/**
 * Configuration.h
 *
 * Basic settings such as:
 *
 * - Type of electronics
 * - Type of temperature sensor
 * - Printer geometry
 * - Endstop configuration
 * - LCD controller
 * - Extra features
 *
 * Advanced settings can be found in Configuration_adv.h
 *
 */
#ifndef CONFIGURATION_H
#define CONFIGURATION_H

/**
 *
 *  ***********************************
 *  **  ATTENTION TO ALL DEVELOPERS  **
 *  ***********************************
 *
 * You must increment this version number for every significant change such as,
 * but not limited to: ADD, DELETE RENAME OR REPURPOSE any directive/option.
 *
 * Note: Update also Version.h !
 */
#define CONFIGURATION_H_VERSION 010100

//===========================================================================
//============================= Getting Started =============================
//===========================================================================

/**
 * Here are some standard links for getting your machine calibrated:
 *
 * http://reprap.org/wiki/Calibration
 * http://youtu.be/wAL9d7FgInk
 * http://calculator.josefprusa.cz
 * http://reprap.org/wiki/Triffid_Hunter%27s_Calibration_Guide
 * http://www.thingiverse.com/thing:5573
 * https://sites.google.com/site/repraplogphase/calibration-of-your-reprap
 * http://www.thingiverse.com/thing:298812
 */

//===========================================================================
//============================= DELTA Printer ===============================
//===========================================================================
// For a Delta printer replace the configuration files with the files in the
// example_configurations/delta directory.
//

//===========================================================================
//============================= SCARA Printer ===============================
//===========================================================================
// For a Scara printer replace the configuration files with the files in the
// example_configurations/SCARA directory.
//

// @section info

// User-specified version info of this build to display in [Pronterface, etc] terminal window during
// startup. Implementation of an idea by Prof Braino to inform user that any changes made to this
// build by the user have been successfully uploaded into firmware.
#define STRING_CONFIG_H_AUTHOR "(none, default config)" // Who made the changes.
#define SHOW_BOOTSCREEN
#define STRING_SPLASH_LINE1 SHORT_BUILD_VERSION // will be shown during bootup in line 1
#define STRING_SPLASH_LINE2 WEBSITE_URL         // will be shown during bootup in line 2

//
// *** VENDORS PLEASE READ *****************************************************
//
// Marlin now allow you to have a vendor boot image to be displayed on machine
// start. When SHOW_CUSTOM_BOOTSCREEN is defined Marlin will first show your
// custom boot image and them the default Marlin boot image is shown.
//
// We suggest for you to take advantage of this new feature and keep the Marlin
// boot image unmodified. For an example have a look at the bq Hephestos 2
// example configuration folder.
//
//#define SHOW_CUSTOM_BOOTSCREEN
// @section machine

// SERIAL_PORT selects which serial port should be used for communication with the host.
// This allows the connection of wireless adapters (for instance) to non-default port pins.
// Serial port 0 is still used by the Arduino bootloader regardless of this setting.
// :[0,1,2,3,4,5,6,7]
#define SERIAL_PORT 0
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

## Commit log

2017-04-03 Initial commit of repository.
    [25mmSlotTNut.stl, 50mLTubeHolder.stl, Cable carrier to cable snake.stl, Cable carrier.stl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]
2017-04-03 Added printing notes and updated README.
2017-04-03 Update assembly notes.
2017-04-03 Added hardware and Bill of Materials.
    [BillofMaterials.xlsx, ModifiedBase.stp]
2017-04-04 Updated Bill of Materials.
    [BillofMaterials.xlsx]

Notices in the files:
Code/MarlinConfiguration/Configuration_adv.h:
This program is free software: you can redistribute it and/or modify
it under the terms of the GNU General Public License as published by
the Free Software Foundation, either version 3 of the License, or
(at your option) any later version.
